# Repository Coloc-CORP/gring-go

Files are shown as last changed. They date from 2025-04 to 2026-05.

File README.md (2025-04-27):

# 💍 Smart BLE Ring Project

---

## 🧠 Team

- 🛠️ **Hardware Engineers**: Mathys Pellen, Pierrick Simon
- 👨‍💻 **Software Engineers**: David Cartier, Marius Chritin

---

## 📜 Project Description

Development of an **ultra-compact smart ring** integrating:
- **Bluetooth Low Energy (BLE) communication**
- **Heart rate (BPM) measurement**
- **Activity and movement tracking**
- **Sleep monitoring**
- **Skin temperature measurement**

Mobile application dedicated to:
- Real-time collection of biometric data
- Visualization and analysis of health information
- Synchronization with **Samsung Health** using **Health Connect API**

---

## 🛠️ Project Architecture

### Hardware
- **Microcontroller**: nRF5340 (Nordic Semiconductor)
- **Main Sensors**:
  - MAX86150: Heart Rate and SpO2
  - BHI260AP: 6-axis IMU (motion detection)
  - MAX30205 (or equivalent): Skin temperature sensor
- **Charging**: Wireless charging with Qi standard (STWLC38 IC)
- **PCB**: Flexible PCB (FPC) for compact integration into a ring
- **Casing**: Titanium ring, machined or 3D printed

### Software
- **Embedded firmware**:
  - Developed with **nRF Connect SDK** (Zephyr RTOS)
  - Standard BLE GATT communication
  - OTA DFU (Firmware update over Bluetooth) supported
- **Android Application**:
  - Developed with **Android Studio**
  - BLE Central communication
  - Integration with **Samsung Health** via **Health Connect**

---

## 📂 Project Folder Structure

```plaintext
/README.md           → Main project documentation
/HW/                 → Hardware designs (schematics, PCB layouts, datasheets)
                     → 3D models of the ring (STEP, STL, F3D formats)
/SW/                 → Embedded firmware for nRF5340 (Zephyr)
                     → Android Studio mobile app project
/doc/                → Specifications, technical documents, research notes
```

---

## 🧩 Technologies and Tools

- **nRF Connect SDK** (Zephyr RTOS, Nordic Semiconductor)
- **Segger Embedded Studio** or **VS Code + nRF Connect Extensions**
- **KiCad** for PCB design
- **OnShape / SolidWorks** for 3D modeling
- **Android Studio** for mobile app development
- **GitHub** for project management and version control

---

## 📈 Roadmap

- [x] Requirements and specifications definition
- [x] Component selection
- [ ] BLE basic firmware development
- [ ] BLE mobile application creation
- [ ] First prototype PCB design
- [ ] Hardware prototype fabrication
- [ ] Full system integration and testing
- [ ] Low-power optimization
- [ ] Final miniaturization and industrialization

---

## ⚡ Inspirations

- Samsung Galaxy Ring
- Oura Ring Gen 3

---

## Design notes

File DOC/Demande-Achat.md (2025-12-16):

## Récapitulatif des composants à acheter

Tous les sites pour acheter chaque composant/carte sont intégrés en hyperlien.

| Composant                | Fonction / Rôle                | Lien / Datasheet / Réf.         | Carte d’évaluation / Dev Kit         |
|--------------------------|-------------------------------|----------------------------------|--------------------------------------|
| nRF5340 (MCU BLE)        | Microcontrôleur principal BLE | [nRF5340](https://www.mouser.fr/ProductDetail/Nordic-Semiconductor/nRF5340-CLAA-R?qs=81r%252BiQLm7BTUbHQUWWib8A%3D%3D&mgh=1&vip=1&utm_id=18189949858&utm_source=google&utm_medium=cpc&utm_marketing_tactic=emeacorp&gad_source=1&gad_campaignid=18189985405&gbraid=0AAAAADn_wf1H5A7hXqZ3Z-MRIcJ73N6WJ&gclid=CjwKCAiA0eTJBhBaEiwA-Pa-hXL2kj0GUdJKz5rNqm_YtVFvSpSPjLrBWhTpHPgSChG9DCrJEowFXRoCWOgQAvD_BwE) | [nRF5340 DK](https://www.mouser.fr/ProductDetail/Nordic-Semiconductor/NRF5340-DK?qs=T94vaHKWudSvpk%2Fi5MmNkA%3D%3D&mgh=1&vip=1&utm_id=18189909961&utm_source=google&utm_medium=cpc&utm_marketing_tactic=emeacorp&gad_source=1&gad_campaignid=18189915556&gbraid=0AAAAADn_wf2LX2m29R1FtorFCg3McUpCX&gclid=CjwKCAiA0eTJBhBaEiwA-Pa-hSZylnIRr_CUexKcZe3W3Hm7M1_NMTNbWYKbaWAjeG-TnCY7hQYBrBoCe3cQAvD_BwE) |
| MAX32664 (PPG)           | Module capteur cardiaque      | [MAX32664](https://www.mouser.fr/ProductDetail/Analog-Devices-Maxim-Integrated/MAX32664GWEA%2bT?qs=MLItCLRbWsyDnR1OLLmFTg%3D%3D) | PCB d'éval conçu, à commander |
| BHI260AP (IMU)           | Accéléro/Gyro 6 axes + MCU    | [BHI260AP](https://www.mouser.fr/ProductDetail/Bosch-Sensortec/BHI260AP?qs=T94vaHKWudTEPTnGI%252BTy9w%3D%3D&srsltid=AfmBOoqDyQJeb3na6sPnhlUFruoI9czkXYRRi1PuOY-V-L53PYxs8R0h) | [BHI260AP Shuttle Board](https://www.mouser.fr/ProductDetail/Bosch-Sensortec/BHI260AP-Shuttle-Board-3.0?qs=sGAEpiMZZMu3sxpa5v1qrpuLb1YRQvRHZemfRhcKQHY%3D) |
| STTS22H (Température)    | Capteur de température        | [STTS22H](https://www.mouser.fr/ProductDetail/STMicroelectronics/STTS22HTR?qs=%252B6g0mu59x7LCfjXXPvLkpg%3D%3D) | [SEN-21262](https://www.mouser.fr/ProductDetail/SparkFun/SEN-21262?qs=9vOqFld9vZWzbY2TLzVlDA%3D%3D&srsltid=AfmBOoovlJG6ulonjrwpkD4eBeJpHDID0WHxTjRv7_asHaaaJilWiW1_) |
| Batterie (test)                | Alimentation                  | [lipo 3.7V 190mAh] https://fr.farnell.com/mikroelektronika/mikroe-2759/batterie-li-ion-3-7v-190mah/dp/2858073   | -                                    |
| DRV2605L (Pilote haptique) | Pilote moteur haptique LRA    | [DRV2605L](https://www.mouser.fr/ProductDetail/Texas-Instruments/DRV2605LTDGSRQ1?qs=bY1dm4K8r4X1ywSIFHWcUw%3D%3D) | [DRV2605L Dev kit](https://fr.rs-online.com/web/p/modules-de-developpement-pour-la-robotique-la-gestion-d-alimentation-et-les-moteurs/1245480?cm_mmc=FR-PLA-DS3A-_-google-_-CSS_FR_FR_PMAX_Catch+All-_--_-1245480&matchtype=&&gclsrc=aw.ds&gad_source=1&gad_campaignid=20578377983&gbraid=0AAAAADkeWNOf1JCgaQc0pjTwe8yyNPBMd&gclid=Cj0KCQiA9OnJBhD-ARIsAPV51xNiMtSwV1MNyEf_7Fm-Ahb4cxmXP-D3dtjudJGbkZPWrh_JE1DPnkkaAiklEALw_wcB) |
| LRA (Moteur haptique)      | Retour haptique (vibration)   | [HD-LA0503-LW28](https://www.mouser.fr/ProductDetail/PUI-Audio/HD-LA0503-LW28?qs=%252BHhoWzUJg4JRddGDY3P1CA%3D%3D) | - |
| Emetteur QI              | Gestion charge sans fil       | [BQ500212A] https://www.mouser.fr/ProductDetail/Texas-Instruments/BQ500212ARGZR?qs=qMm2Sc3MXu62Fost5xc9Dg%3D%3D | PCB d'éval conçu, à commander |
| Recepteur QI             | Gestion charge sans fil       | [BQ51003] https://www.mouser.fr/ProductDetail/Texas-Instruments/BQ51003YFPR?qs=QCUnHQQYO1rRiXeciFj5cA%3D%3D | PCB d'éval conçu, à commander |
| Régulateur / LDO / Chargeur| Régulation tension / charge batterie | [BQ25120A] https://www.mouser.fr/ProductDetail/Texas-Instruments/BQ25120AYFPR?qs=BZBei1rCqCBtbT0X52DCMQ%3D%3D | PCB d'éval conçu, à commander |
| Antenne BLE              | Communication sans fil        | (À définir)                      | Intégré à la carte d'éval nRF5340 DK                                    |

Chaque composant est relié à la carte principale (MCU nRF5340) via des interfaces standards (I²C/SPI pour les capteurs, GPIO pour l’antenne, etc.). Les cartes d’évaluation associées permettent de tester individuellement chaque composant avant intégration sur le PCB final.

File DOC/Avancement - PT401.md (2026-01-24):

*Aperçu de l'avancement au 24 janvier 2026 de notre projet **GRING-GO**.*
## Organisation / documentation

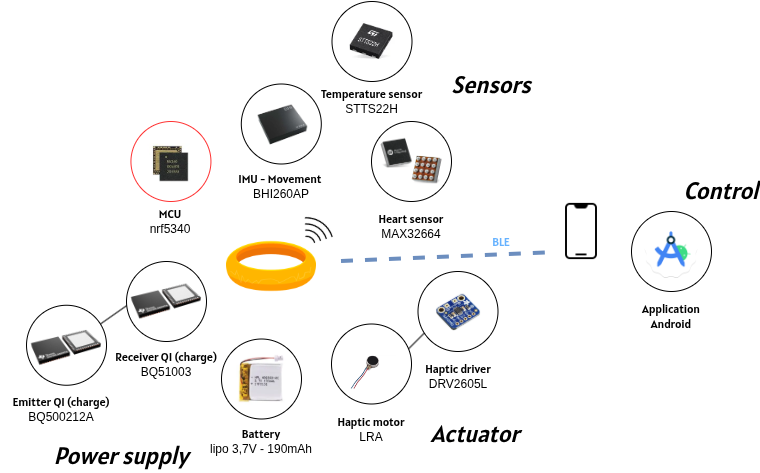
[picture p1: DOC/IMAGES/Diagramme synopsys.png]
Diagramme synopsys.png


Différents documents rédigés : 
- Cahier des charges
- Diagramme de Gantt (organisation + attribution des tâches)
*Vous pouvez retrouver 2 fichiers pdf : Gantt_Gring-go.pdf & Gantt_Gring-go-V2.pdf. La deuxième version incluant les retards.* 
- Répartition horaire

Suivi organisé : [Projet gring-go Github](https://github.com/Coloc-CORP/gring-go)
On retrouve sur ce git le développement entier séparé en différentes branches. L'utilisation des *Tasks*, pour répartir les tâches et avoir une vue d'ensemble de l'état d'avancement du projet.
## Electronique

### Conception des Cartes d'Évaluation Custom

Face à l'indisponibilité ou au coût prohibitif des kits d'évaluation constructeurs officiels, nous avons pris l'initiative de concevoir et produire nos propres solutions de test pour valider les briques technologiques critiques.

#### Conception et Prototypage
Deux cartes d'évaluation spécifiques ont été routées et fabriquées :
* **Module Power & Charge :** Dédié au **BQ25120A** pour valider la régulation du rail 3.0V (indispensable pour le nRF5340) et la gestion de la charge batterie.
* **Module Biométrique :** Support spécifique pour le **MAX32664** et son capteur optique associé, permettant de tester la qualité du signal brut avant l'intégration finale.

#### État de l'Avancement Hardware
* **Statut actuel :** Les circuits imprimés (PCB) et l'ensemble des composants ont été reçus.
* **Phase de Montage :** Nous entamons actuellement le soudage des composants CMS (Composants Montés en Surface).
* **Validation :** Une fois le soudage terminé, nous procéderons aux tests de mise sous tension et à la validation de la communication I2C avec le nRF5340 pour tester "en réel" les drivers précédemment développés.

### Étude de Consommation Théorique

En parallèle du développement, une étude de consommation a été réalisée pour valider la viabilité énergétique du produit.

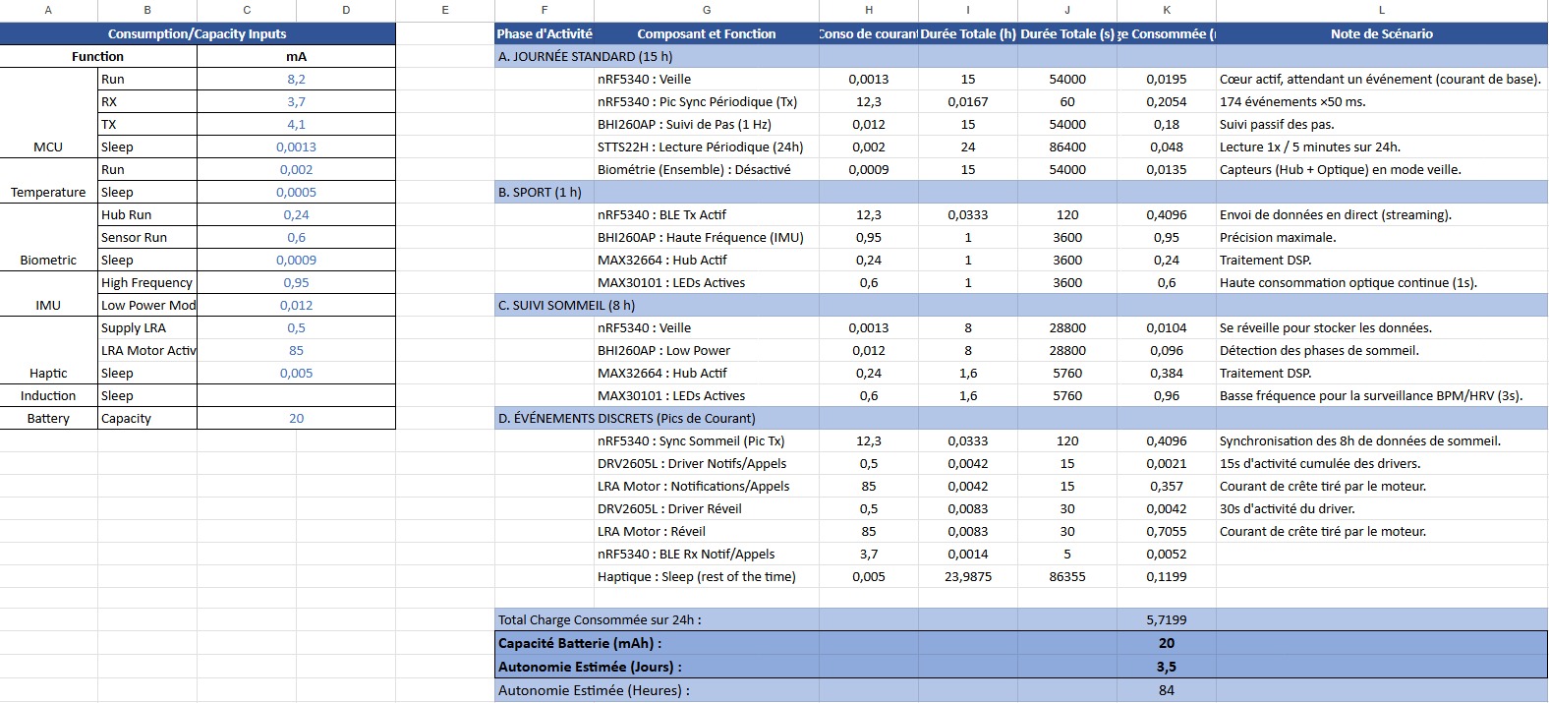
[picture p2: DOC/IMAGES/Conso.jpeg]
Conso


* **Objectif :** Valider une autonomie approximative satisfaisante plutôt que de déterminer une valeur précise dès maintenant.
* **Résultats :** L'étude confirme une autonomie théorique d'environ **3 jours et demi** avec une utilisation normale (polling régulier des capteurs et notifications BLE avec vibration).
* **Validation :** Ce résultat valide les choix d'architecture (rail 3.0V optimisé et modes basse consommation des hubs de capteurs) et assure que le dispositif répond aux attentes qu'on a d'un "wearable".

### Système d'alimentation par induction

Nous avons réalisés une étude comparative sur les modes de transfert d'énergie sans fil, ce qui m'a conduit à valider une architecture basée sur la norme Qi.

#### Architecture système et choix des composants

L'objectif est d'intégrer un système complet dans un volume restreint (type bague connectée). Initialement, l'architecture retenue se décomposait ainsi:

- **Émetteur (Boîtier) :** Utilisation du **BQ500212A**, nécessitant un convertisseur Boost pour stabiliser l'alimentation 5V.
    
- **Récepteur (Bague) :** Le couple **BQ51003** et **BQ25120A** avait été choisi. Le BQ51003 gère la réception , tandis que le BQ25120A fait office de PMIC pour gérer le "Power Path".

Cependant, la conception d'un premier PCB pour ces composants spécifiques a révélé des contraintes de fabrication imprévues : la largeur nécessaire entre les vias était trop faible, rendant le coût de production du PCB prohibitif pour une phase de prototypage.

#### Adaptation pour la phase de test

Afin de valider le fonctionnement sans exploser le budget, j'ai modifié l'architecture pour cette version de test. Sur la partie bague, j'ai remplacé les composants initiaux par un récepteur **BQ51013** couplé à un chargeur **MCP73831T**.

Les cartes d'évaluation constructeur étant trop chères, j'ai conçu mon propre PCB de test sur **KiCad**. Le design est validé et permet de contourner les coûts élevés du premier prototype.

#### Conception hardware et dimensionnement

Le travail de conception s’est concentré sur l'optimisation de l'antenne et de la résonance :

- **Bobinage :** J'utilise du fil de cuivre de 0,22 mm. L'idée est de réaliser un montage type "fil de Litz" pour limiter l'effet de peau et maximiser le passage du courant à haute fréquence.
    
- **Accord de fréquence :** L’étape critique est le calcul des condensateurs de résonance $C_1$ et $C_2$ pour accorder l'antenne sur la fréquence cible de 100 kHz. L’ajout de feuilles de ferrite est également prévu pour canaliser le flux.

#### Prochains pas

Le PCB de test sur KiCad est réussi. Actuellement, je suis en attente de la réception des composants pour lancer l'assemblage. Pour effectuer les premiers essais de charge, j'ai également commandé une petite batterie LiPo, en sélectionnant le modèle le moins cher et le plus compact possible.

## Software

### Programmation embarqué

#### Développement embarqué NRF5340

Le développement logiciel repose sur le processeur **nRF5340** (Dual-core ARM Cortex-M33). L'architecture a été conçue pour être modulaire sous **Zephyr RTOS**, en respectant notre diagramme UML qui sépare strictement la gestion des périphériques de la logique applicative.

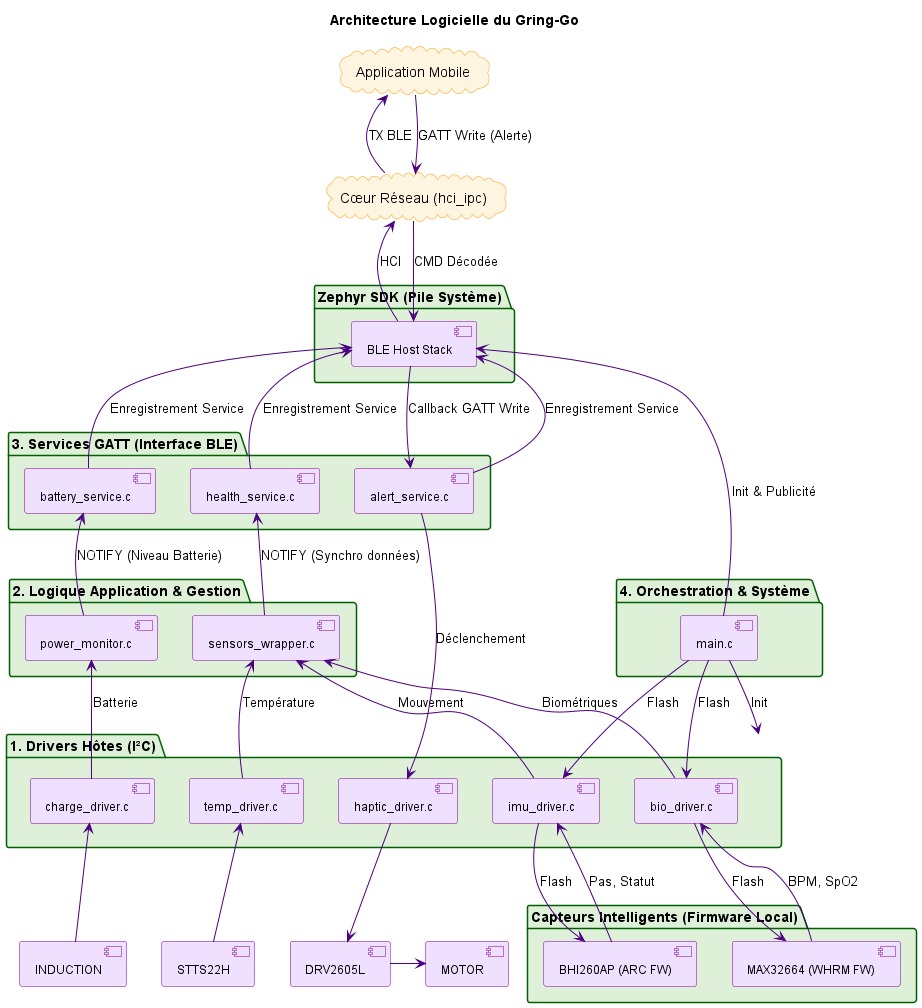
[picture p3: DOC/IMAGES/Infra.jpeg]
Infra


*Ce diagramme UML a été réalisé par l'écriture d'un code PlantUML.*

##### Travaux Réalisés : Couche Drivers
La phase de développement des drivers de bas niveau est désormais terminée. Ce travail a inclus :
* **Communication I2C & Comportement :** Écriture des drivers pour l'IMU (**BHI260AP**), le capteur biométrique (**MAX32664**), le capteur de température (**STTS22H**) et le gestionnaire de charge (**BQ25120A**).
* **Injection de Code (Sensor Fusion) :** Implémentation de la logique d'injection des données accélérométriques de l'IMU vers le capteur cardiaque pour la compensation de mouvement, garantissant la précision des mesures lors d'activités physiques.
* **Gestion de l'Énergie :** Configuration des registres pour optimiser l'autonomie (Deep Sleep, Ship Mode).
* ...

##### Prochaines Étapes : Intégration et Bluetooth
Le code est prêt pour la phase de tests réels sur les composants. La suite du développement portera sur :
* **Communication BLE :** Développement de la stack Bluetooth Low Energy.
* **Synchronisation Application :** Travail en collaboration avec **David** pour mapper les structures de données sur les services GATT afin d'assurer une communication fluide avec l'application mobile en cours de développement.

### Application Android

L'application Android est développé en JAVA sur Android Studio. 
Nous sommes passés sur une première phase de réflexion de l'architecture avec la définitions des différents *fragments* de l'application, c'est à dire les différentes fenêtres.

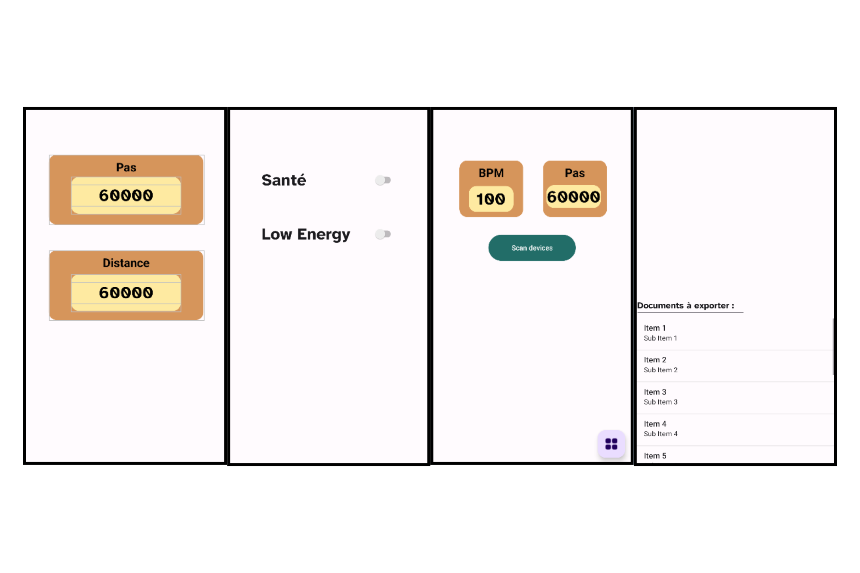
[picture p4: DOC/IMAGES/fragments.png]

*Différents fragments créés 

Les fonctions de découverte Bluetooth à été mise en place. Le reste de la communication va se baser sur [Android-BLE-Library](https://github.com/NordicSemiconductor/Android-BLE-Library). 

Suite à l'appui du bouton *Scan Devices*, la liste d'appareils bluetooth apparaît et l'on peut choisir l'appareil bluetooth auquel s'appairer (le nrf5340). 

On retrouve une autre thématique qui est l'autorisation de permissions. 

## Retards (justification)

On retrouve de légers retards sur 2 points : 
- La partie hardware avec notamment l'alimentation boitier : celle-ci a pris du retard avec l’absence de composants.
- L'application Android est plus lente à développer que prévu car c'est un nouvel environnement sur lequel nous débutons. C'est pour cela que le temps d'adaptation n'est pas a négligé

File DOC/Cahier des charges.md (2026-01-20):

## Introduction

La formation d'ingénieur de l'ESISAR est une formation permettant de de construire les connaissances et compétences de l'ingénieur que celui-ci pourra être confronté dans sa carrière professionnelle. Cela est fait de différentes façon lors des différents cours suivis dans l'école mais la formation passe par une étape très importante : la mise en situation réelle.

Etre en entreprise, c'est faire continuellement des *projets*. En effet, ce sont autour de ces entités que grand nombre d'entre nous naviguent en entreprise. Ceux-ci se déroulent en plusieurs étapes et requièrent un large spectre de compétences pour les mettre à bien.

Le projet, choisi par nous-mêmes, est le projet d'une bague connectée que l'on appelle *Gring-Go*. Le travail va être effectué en passant de la spécification du projet au développement des différentes composantes, en passant par les différents tests démonstratifs pour enfin avoir un produit complet répondant aux différentes problématiques.

C'est un projet qui se déroule sur 9 semaines avec un nombre d'heures alloué au projet d'une centaine d'heures pour chaque collaborateur.

---
## Objectifs

### Objectifs principaux
-  Avoir un suivi des données corporelles en temps réel
-  Pouvoir interagir avec la bague via un système Android
-  Choisir les composants adéquats pour la réalisation du cahier des charges
-  Avoir un suivi des données corporelles dans le temps
-  Notifier sensoriellement l'utilisateur lors d'évenements sur le téléphone 
-  Avoir un gabarit adapté à l'utilisation en tant que bague

### Objectifs transverses
-  Conduire l'organisation et le management du projet de bout en bout
-  Renforcer ses compétences techniques en autonomie

---
## Diagramme du projet

Diagramme synopsys.png

---
## Description fonctionnelle

1. FP : Le produit doit permettre à l'utilisateur de suivre ces données biométriques.

2. FP : Le produit doit permettre à l'utilisateur de suivre ces données d'activité physique.
3. FP : Le produit doit permettre à l'utilisateur d'être notifier d'évênements sur le téléphone.
4. FC : Le produit doit être confortable à porter (forme agréable, matériau confortable)
5. FC : L'autonomie du produit doit être suffisamment élevé (1 semaine d'autonomie).
6. FC : La distance de communication doit être suffisamment élevé (5 m)
7. FC : Le produit doit être convenablement réactif (mesures <1 min)

*Provisoire*
1. FP : Le produit doit permettre à l'utilisateur de suivre son sommeil
2. FP : Le produit doit permettre à l'utilisateur d'avoir un indicateur sur son stress

3. FC : Le produit doit être résistant à l'eau (IP)
4. FC : Le produit peut se charger sans fil (charge par induction)

---
## Budget

Un budget entre 300 et 400 € à été annoncé pour la réalisation du projets (matériel, prestations, composants).

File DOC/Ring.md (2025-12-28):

# 💍 Projet Bague Connectée BLE - Santé & Bien-être

## 🎯 Objectif

Créer une **bague connectée** ultra-compacte, élégante et rechargeable sans fil, capable de :
- Suivre la fréquence cardiaque
- Mesurer la SpO2 (oxygène dans le sang)
- Évaluer le stress
- Compter les pas et suivre l’activité physique
- Suivre les phases de sommeil
- Mesurer la température corporelle
- Se connecter à Samsung Health via Bluetooth Low Energy (BLE)

---

## 🧩 Architecture générale

| Composant                  | Fonction                                                     |
| -------------------------- | ------------------------------------------------------------ |
| **nRF5340 (Nordic)**       | Microcontrôleur principal avec BLE                           |
| **MAX86150 / MAX30102**    | Capteur PPG (fréquence cardiaque, SpO2, stress)              |
| **BHI260AP / LSM6DSOX**    | IMU pour mouvement, podomètre, détection du sommeil          |
| **STTS22H**                | Capteur de température corporelle                            |
| **Batterie LiPo 10-20mAh** | Alimentation, rechargeable sans fil                          |
| **STWLC38**                | Récepteur de recharge sans fil (Qi) avec protection intégrée |
| **PCB flexible (FPC)**     | Support du circuit miniature                                 |
| **Boîtier titane**         | Enveloppe solide, légère et hypoallergénique                 |

---

## 🔋 Alimentation & Recharge

- **Recharge sans fil Qi** via un chargeur personnalisé
- Basé sur **STWLC38**, compatible Qi 1.2, avec protection intégrée
- Antenne bobinée sur FPC autour de la bague
- Batterie : **LiPo 3.7V** entre 10 et 20 mAh, charge lente pour préserver la durée de vie

---

## 📱 Fonctionnalités principales

| Fonction                      | Capteurs nécessaires                     | Détail technique                                   |
|-------------------------------|------------------------------------------|---------------------------------------------------|
| Fréquence cardiaque           | MAX86150 / MAX30102                      | PPG infrarouge, données envoyées en BLE           |
| SpO2                          | MAX86150 / MAX30102                      | Analyse des variations d’intensité lumineuse      |
| Stress / HRV                  | PPG                                      | Analyse de la variabilité cardiaque (HRV)         |
| Suivi des pas (podomètre)     | BHI260AP / LSM6DSOX                      | Accéléromètre et algorithmes de step counting     |
| Suivi de sommeil (phases)     | PPG + IMU                                | Fusion des données pour estimer les cycles        |
| Température corporelle        | STTS22H                                  | Mesure en contact avec la peau (intérieur bague)  |

---

## 📶 Connexion à Samsung Health

- **BLE Standard HRM (Heart Rate Monitor Profile)** reconnu par Samsung Health
- Via **nRF Connect SDK** (Zephyr RTOS) ou Nordic SDK
- Possibilité de développer une **application Android compagnon** pour collecter, afficher et éventuellement **transférer via Health Connect** les données vers Samsung Health

---

## 🛠️ Logiciels & Développement

- **Firmware :**
  - **nRF Connect SDK** avec Zephyr RTOS (Langage C)
  - IDE recommandé : **nRF Connect for VS Code** ou **Segger Embedded Studio**
- **Conception PCB :**
  - Outils : **KiCad**, **Altium Designer**
  - Type : **Flexible PCB (FPC)** ultra-fin
- **Modélisation 3D du boîtier :**
  - Fusion 360 / SolidWorks
  - Impression SLA ou CNC pour prototypage
  - Matériau : **Titane** (durable, hypoallergénique)

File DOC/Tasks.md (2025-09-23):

# Découpage des tâches et estimations de temps - Projet Gring-Go
## Mathys : 

- Orga : 7H
  - Identification des grandes parties et objectifs du projet : 2H
  - Répartition de la charge de travail : 1H
  - Découpage des taches : 1.5H
  - Estimation de temps des tâches et Gantt : 2.5H
- DOC : 13H
  - Cahier des charges : 3H
  - Spécifications : 2H
  - Hardware Design Description : 10H
- HW : 12H
  - Choix des composants : 12H
    - Accélero / Podo : 2H
    - PPG / Sp02 : 2H
    - Temperature : 2H
    - Microcontroleur : 2H
    - HP ou Micro ? : 2H
    - Antenne BLE : 2H
- SW : 32H
  - Embarqué : 32H
    - Traitement des données capteurs : 9H
      - PPG : 3H
      - Accéléro : 3H
      - Temp : 3H
    - Communication capteur / micro : 4H
    - Commande de l'actionneur (HP ou micro) : 7H
    - Communication des données vers Appli : 5H
      - Transmission des données capteurs : 2.5H
      - Réception de commandes : 2.5H
    - Gestion énergétique : 7H
      - Implémentation des modes de veille du micro : 3H
      - Gestion des capteurs : 4H
- Modélisation 3D : 33H
  - Plans de la bague : 5H
  - Modèle : 28H
- Etude de consommation : 13H
  - Etablir un plan de mesures de consommations : 2H
  - Réaliser les mesures : 7H
  - Interpréter les mesures et les documenter : 4H 

TOTAL : 110H

TOTAL D'HEURES EN SEANCES : 28H + 28H = 56H

TOTAL D'HEURES EN PERSO : 54H

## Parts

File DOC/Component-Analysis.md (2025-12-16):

# 📊 Component Comparison Tables — Smart Ring Project

---

## 1. Microcontroller (MCU BLE)

| Model            | Dimensions (mm) | Mass | Consumption (Active / Sleep) | Supply Voltage | Flash / RAM | Interfaces | Special Features | Eval Kit Availability | Price (€) | Notes |
|------------------|-----------------|------|------------------------------|----------------|-------------|------------|------------------|-----------------------|-----------|-------|
| **nRF5340** (Nordic) |                 |      |                              |                |             |            |                  |                       |           | Le plus utilisé sur le marché pour les memes usages donc aussi le plus de commu pour de l'aide potentielle dans forums, possède toutes les fonctions nécessaires + multi thread + RTOS |
|                  |                 |      |                              |                |             |            |                  |                       |           |       |
|                  |                 |      |                              |                |             |            |                  |                       |           |       |

---

## 2. Heart Rate Sensor (PPG + Sp0²)

| Model                     | Dimensions (mm)    | Mass | Consumption (Act / Sleep) | Supply Voltage    | Interface | Acc / Perf | Integrated LEDs | Module / Sensor | VIL / VIH        | Price (€) | Notes |
|---------------------------|--------------------|------|---------------------------|-------------------|-----------|------------|-----------------|-----------------|------------------|-----------|-------|
| **MAX32664** (Analog Devices) | 3.87 x 3.87 x 0.64 | 22mg |                           | 1.71 - 3.63V      | I²C / SPI |            | No              | Module          | 0.3 / 0.7 VDD    | 6.12      | Besoin d'un capteur optique avec données brutes en sortie |
| MAX30101 (Analog Devices) | 5.6  x 3.3  x 1.55 | 33mg | **0.6mA / 0.7µA**             | 1.7 - 2V (5V LED) | I²C       | 18-bits    | Yes             | Sensor          | 0.3 / 0.7 VDD    | 10.23     | **PIM438**| 
| NJL5313R (Nisshinbo)      | 3.15 x 6.00 x 0.65 | **17mg** | 15mA                      | 3.5V              | -         |            | Yes             | Sensor          | -                | 5.18      | Consomme trop et mauvaise disponibilité      |

---

## 3. IMU (Accelerometer + Gyroscope)

| Model            | Dimensions (mm)    | Mass | Consumption (Active / Sleep) | Supply Voltage | Interface | Axes | Accuracy | VIL / VIH        | Price (€) | Notes |
|------------------|--------------------|------|------------------------------|----------------|-----------|------|----------|------------------|-----------|-------|
| **BHI260AP (Bosch)** | 3.6 x 4.1 x 0.83   |      | 249µA / 8µA                  | 1.8V           | I²C / SPI | 6    |          | 0.3 / 0.7 VDD    | 6.05      | **MCU intégré qui traite localement les données : beaucoup plus simple à implémenter**, Dev board 13$ |
| LSM6DSOX (ST)    |**2.5 x 3   x 0.83**|      | **170-26µA  / 3µA**          | 1.7 - 3.6V     | I²C / SPI | 6    |          | 0.3 / 0.7 VDD    | **3.62**  | ABX00101 10$, STEVAL 15$      |
|                  |                    |      |                              |                |           |      |          |                  |           |       |

---

## 4. Temperature Sensor

| Model        | Dimensions (mm) | Mass | Consumption  | Supply Voltage | Interface   | Accuracy | Special Features | Price (€) | Notes |
|--------------|-----------------|------|--------------|----------------|-------------|----------|------------------|-----------|-------|
| **STTS22H (ST)** | 2.0 x 2.0 x 0.5 |      | **120 / 1.75 µA**| 1.5 - 3.6      | I²C / SMBus | 0.25°C   |                  | 1.45      | **SEN-21262 6$**|
| TMP117       | **1.5 x 0.95 x 0.5**|      | 135 / 3.5 µA | 1.7 - 5.5      | I²C / SMBus | **0.1°C**    |                  | 1.92      | SEN-15805 17$, ADA4821 14$      |

---

## 5. Battery

| Model | Capacity (mAh) | Mass | Dimensions (mm) | Thickness (mm) | Voltage (Nominal / Range) | Protection Circuit | Certification | Price (€) | Notes |
|-------|----------------|------|-----------------|----------------|---------------------------|--------------------|---------------|-----------|-------|
|       |                |      |                 |                |                           |                    |               |           |       |
|       |                |      |                 |                |                           |                    |               |           |       |

---

## 6. Wireless Charging IC

| Model | Dimensions (mm) | Mass | Supply Voltage | Output Voltage | Efficiency | Qi Standard Support | Features | Price (€) | Notes |
|-------|-----------------|------|----------------|----------------|------------|---------------------|----------|-----------|-------|
|       |                 |      |                |                |            |                     |          |           |       |
|       |                 |      |                |                |            |                     |          |           |       |

---

## 7. Wireless Charging Coil

| Model | Diameter (mm) | Mass | Thickness (mm) | Inductance (µH) | Resistance (Ω) | Efficiency | Compatible ICs | Price (€) | Notes |
|-------|---------------|------|----------------|-----------------|----------------|------------|----------------|-----------|-------|
|       |               |      |                |                 |                |            |                |           |       |
|       |               |      |                |                 |                |            |                |           |       |

---

## 8. Regulator / LDO

| Model | Dimensions (mm) | Output Voltage | Quiescent Current | Dropout Voltage | Max Current | Noise Level | Price (€) | Notes |
|-------|-----------------|----------------|-------------------|-----------------|-------------|-------------|-----------|-------|
|       |                 |                |                   |                 |             |             |           |       |
|       |                 |                |                   |                 |             |             |           |       |

---

## 9. BLE Antenna

| Model | Type (Ceramic / PCB) | Dimensions (mm) | Mass | Gain (dBi) | Frequency | Matching Required | Price (€) | Notes |
|-------|----------------------|-----------------|------|------------|-----------|-------------------|-----------|-------|
|       |                      |                 |      |            |           |                   |           |       |
|       |                      |                 |      |            |           |                   |           |       |

## 10. Actionneur (Comparaison)

| Actionneur | Mode de Fonctionnement | Avantages pour une Bague | Inconvénients / Impact Physique | Choix |
| :--- | :--- | :--- | :--- | :--- |
| **Moteur Haptique (LRA/ERM)** | Vibration discrète | **Retour personnel et silencieux.** Faible consommation cumulée (pics courts). | Nécessite un volume minimal (épaisseur) et un driver (DRV2605L). | **CHOISI** |
| **Haut-Parleur / Buzzer** | Son / Alerte audible | Peut attirer l'attention de l'utilisateur sans contact. | **Nécessite une chambre acoustique.** Retour non-discret (entendue par l'entourage). Haute consommation continue. | REJETÉ |
| **Microphone** | Acquisition audio | Permet la commande vocale ou l'enregistrement (si requis). | **Non un actionneur.** Nécessite un ADC / DSP pour le traitement et une forte consommation. | REJETÉ |

---

## 11. Composants Haptiques 

| Model | Dimensions (mm) | Mass | Consumption (Active / Sleep) | Supply Voltage | Interface | Special Features | Eval Kit Availability | Price (€) | Notes |
|---|---|---|---|---|---|---|---|---|---|
| **Pilote DRV2605L (TI)** | 1.5 x 1.5 x 0.6 | | **0.5 mA / 4.1 µA** | 1.8 - 3.3V | I²C | Bibliothèque de 123 effets ROM intégrée. | DRV2605LEVM (Abordable) | 2.15 | Utilisation du mode Bibliothèque pour décharger le nRF5340. |
| **Moteur LRA** (Ex: HD-EMC0503-LW27) | $5 \text{ x } 1.8$ (épaisseur) | < 1g | **85 mA** (pic) | 2.7 - 3.3V | PWM | Le seul LRA compatible avec l'épaisseur d'une bague. | N/A | 1.50 | Courant de pointe important (85 mA) mais très courte durée (Duty Cycle faible). |

---

## Final choices

| **Component** | **Dimensions (mm)** | **Consumption (Active / Sleep)** | **Supply Voltage** | **Interface** | **Accuracy / Performance** | **Special Features** | **Price (€)** | **Notes** |
|---------------|----------------------|----------------------------------|---------------------|---------------|-----------------------------|-----------------------|---------------|-----------|
| MCU           | nRF5340              |                                  |                     |               |                             | Multi-thread, RTOS    |               | Le plus utilisé sur le marché, grande communauté |
| Heart Sensor (PPG) | MAX32664          |                                  | 1.71 - 3.63V        | I²C / SPI     |                            | Besoin d'un capteur optique, données brutes | 6.12          | Module, nécessite capteur optique externe |
| IMU           | BHI260AP             | 249µA / 8µA                    | 1.8V         | I²C / SPI     | 6 axes                     |                      | 6.05          | **MCU intégré qui traite localement les données : beaucoup plus simple à implémenter**, Dev board 13$ |
| Temp Sensor   | STTS22H              | 120 / 1.75 µA                     | 1.5 - 3.6V         | I²C / SMBus   | 0.25°C                      |                      | 1.45          | SEN-21262 6€ |
| **Haptic Driver** | **DRV2605L** | **0.5 mA / 4.1 µA** | **1.8 - 3.3V** | **I²C** | **N/A** | **Bibliothèque ROM intégrée** | **2.15** | Pilote basse consommation pour décharger le MCU. |
| **Haptic Motor** | **LRA** | **85 mA / 0 mA** | **2.7 - 3.3V** | **PWM** | **Discret** | **Ultra-plat (1.8mm)** | **1.50** | Courant de pointe important mais durée d'activation très courte. | Battery       |                      |                                  |                     |               |                             |                       |               |           |
| Wireless Charging IC |                |                                  |                     |               |                             |                       |               |           |
| Charging Coil |                      |                                  |                     |               |                             |                       |               |           |
| Regulator / LDO |                     |                                  |                     |               |                             |                       |               |           |
| BLE Antenna   |                      |                                  |                     |               |                             |                       |               |           |
| Other         |                      |                                  |                     |               |                             |                       |               |           |

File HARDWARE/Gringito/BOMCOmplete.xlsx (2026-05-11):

Quantité | Références | Type | Valeur / MPN | Boîtier | Spécifications et Filtres (Mouser / Digi-Key) | ref | Ref mouser | Prix | Stock ? | A commander | Prix a commander
1 | U4 | Puce | BQ500212ARGZR | VQFN-48 | Contrôleur Émetteur Qi |  | https://www.mouser.fr/c/?q=BQ500212ARGZR | 7.62 | 6 | 0 | 0
1 | U6 | Puce | BQ51013BRHLR | VQFN-20 | Contrôleur Récepteur Qi |  | https://www.mouser.fr/ProductDetail/Texas-Instruments/BQ51013BRHLR | 3.1 | 1 | 2 | 6.2
2 | U3, U5 | Puce | CSD97376Q4M | VSON-8 | Power Stage NexFET |  | https://www.mouser.fr/ProductDetail/Texas-Instruments/CSD97376Q4M?qs=7GxONfNUZSgNG7s2u94qUg%3D%3D | 1.85 | 0 | 6 | 11.1
2 | U1, U8 | Puce | PTPS7A2033PDBVR | SOT-23-5 | LDO 3.3V |  | https://www.mouser.fr/ProductDetail/Texas-Instruments/TPS7A2033PDBVR?qs=hd1VzrDQEGjk%2FOBnRfKB4A%3D%3D | 0.275 | 0 | 6 | 1.65
1 | U2 | Puce | INA199A1DCKR | SC-70-6 | Amplificateur de mesure de courant |  | https://www.mouser.fr/ProductDetail/Texas-Instruments/INA199A1DCKR?qs=v3hU%2FV0XOahkyIKIBScY5Q%3D%3D | 0.499 | 0 | 3 | 1.497
1 | U7 | Puce | MCP73831T-2ATI/OT | SOT-23-5 | Chargeur Li-Ion |  | https://www.mouser.fr/ProductDetail/Microchip-Technology/MCP73831T-2ATI-OT?qs=yUQqVecv4qsZbioEUu%252B83g%3D%3D | 0.654 | 1 | 2 | 1.308
1 | C7 | Condensateur | 33pF | 805 | Diélectrique C0G/NP0, Tension 50V min | VJ0805A330KXAAC | https://www.mouser.fr/ProductDetail/Vishay-Vitramon/VJ0805A330KXAAC?qs=%252BzNVVDDlEaF%2FJI7KaxLPoQ%3D%3D | 0.189 | 0 | 10 | 1.89 | Prix total
2 | C12, C17 | Condensateur | 4.7nF (4700pF) | 805 | Diélectrique C0G/NP0, Tension 50V min | CGA4C2C0G1H472J | https://www.mouser.fr/ProductDetail/TDK/CGA4C2C0G1H472J060AA?qs=FxQuwy19cyCgdYzJw5%252BHfA%3D%3D | 0.071 | 0 | 20 | 1.42 | 63.223
4 | C1, C20, C36, C42 | Condensateur | 0.01µF (10nF) | 805 | Diélectrique C0G/NP0, Tension 50V min | CGA4C2C0G1H103J | https://www.mouser.fr/ProductDetail/TDK/C2012C0G1H103J060AA?qs=dfay7wIA1uESihXTlxZAiQ%3D%3D | 0.103 | 0 | 20 | 2.06
2 | C32, C44 | Condensateur | 22nF | 805 | Diélectrique C0G/NP0, Tension 50V min | CGA4J2C0G1H223J | https://www.mouser.fr/ProductDetail/TDK/CGA4J2C0G1H223J125AA?qs=NRhsANhppD%252B%2Fmt276RAXag%3D%3D | 0.12 | 0 | 10 | 1.2
2 | C34, C43 | Condensateur | 0.47µF (470nF) | 805 | Diélectrique X7R, Tension 50V min | C0805C474J5REC7210 | https://www.mouser.fr/ProductDetail/KEMET/C0805C474J5REC7210?qs=55YtniHzbhBIB%252B2OjgsYHA%3D%3D | 0.153 | 0 | 10 | 1.53
5 | C37, C38, C39, C40, C41 | Condensateur | TDB | 805 | Prévoir des assortiments C0G de quelques nF pour le réglage au labo |  |  |  |  |  | 0
5 | Pour C37 à C41 | Condensateur | 2.2 nF (2200 pF) | 805 | Diélectrique C0G/NP0, Tension 50V min | CGA4J3C0G2E222J | https://www.mouser.fr/ProductDetail/TDK/CGA4J3C0G2E222J125AA?qs=FxQuwy19cyAnpWAkJxMUqQ%3D%3D | 0.093 |  | 10 | 0.93
5 | Pour C37 à C41 | Condensateur | 1 nF (1000 pF) | 805 | Diélectrique C0G/NP0, Tension 50V min | AC805JRNPO0BN102 | https://www.mouser.fr/ProductDetail/YAGEO/AC0805JRNPO0BN102?qs=WS5Jv%252B%252Bx1qWv6SGJfntmZw%3D%3D | 0.089 | 0 | 10 | 0.89
5 | Pour C37 à C41 | Condensateur | 470 pF | 805 | Diélectrique C0G/NP0, Tension 50V min | CC0805JPNPO9BN471 | https://www.mouser.fr/ProductDetail/YAGEO/CC0805JPNPO9BN471?qs=7s%252B3O6pAiyArhfcZRyQSXQ%3D%3D | 0.037 | 0 | 10 | 0.37
5 | Pour C37 à C41 | Condensateur | 220 pF | 805 | Diélectrique C0G/NP0, Tension 50V min | CGA4C4C0G2W221J060AA | https://www.mouser.fr/ProductDetail/TDK/CGA4C4C0G2W221J060AA?qs=Zt%252BKPUOg4ocV%252BjuYZYAGHQ%3D%3D | 0.077 | 0 | 10 | 0.77
5 | Pour C37 à C41 | Condensateur | 100 pF | 805 | Diélectrique C0G/NP0, Tension 50V min |  | AVEC C16 C18 |  |  |  | 0
5 | Pour C37 à C41 | Condensateur | 47 pF | 805 | Diélectrique C0G/NP0, Tension 50V min | C0805C470JDGACTU | https://www.mouser.fr/ProductDetail/KEMET/C0805C470JDGACTU?qs=HkDAmeg8w%252BfhZX5bPX%2F3Fg%3D%3D | 0.19 | 0 | 10 | 1.9
5 | Pour C37 à C41 | Condensateur | 22 pF | 805 | Diélectrique C0G/NP0, Tension 50V min | VJ0805A220JXCCW1BC | https://www.mouser.fr/ProductDetail/Vishay-Vitramon/VJ0805A220JXCCW1BC?qs=5N7VPDfziMRebYDFq5t7Jw%3D%3D | 0.12 | 0 | 10 | 1.2
4 | C2, C13, C25, C29 | Condensateur | 10µF | 805 | Diélectrique X5R ou X7R, Tension 50V min | GRM21BR61H106KE43L | https://www.mouser.fr/ProductDetail/Murata-Electronics/GRM21BR61H106KE43L?qs=lYGu3FyN48cBZlIduWKclg%3D%3D | 0.109 | 0 | 20 | 2.18
2 | C9, C14 | Condensateur | 4.7µF | 805 | Diélectrique X5R ou X7R, Tension 25V min | CGA4J1X7R1H475K125AC | https://www.mouser.fr/ProductDetail/TDK/CGA4J1X7R1H475K125AC?qs=PqoDHHvF64%252BmskN2S82T2g%3D%3D | 0.224 | 0 | 10 | 2.24
12 | C3, C4, C8, C10, C15, C22, C26, C27, C30, C31, C33, C35 | Condensateur | 1µF | 805 | Diélectrique X7R, Tension 25V min | C2012X7R1H105K | https://www.mouser.fr/ProductDetail/TDK/C2012X7R1H105K125AB?qs=NRhsANhppD9AlYlb8kBg7Q%3D%3D | 0.099 | 0 | 30 | 2.97
6 | C5, C6, C11, C23, C24, C28 | Condensateur | 0.1µF (100nF) | 805 | Diélectrique X7R, Tension 50V min | KAF21KR72A104KL | https://www.mouser.fr/ProductDetail/KYOCERA-AVX/KAF21KR72A104KL?qs=Jm2GQyTW%2FbiUCISqVwD%2FLA%3D%3D | 0.101 | 0 | 20 | 2.02
4 | C16, C18, C19, C21 | Condensateur | 0.1µF (100nF) | 1206 | Diélectrique C0G/NP0, Tension 50V min | C3216C0G2A104J6C | https://www.mouser.fr/ProductDetail/TDK/C3216C0G2A104J160AC?qs=sO%2FZ8XQFeM2ox3y9zt3TJw%3D%3D | 0.362 | 0 | 20 | 7.24
1 | R3 | Résistance | 20 mΩ | 805 | Tolérance 1%, Current Sense, Puissance 0.25W ou 0.5W | 652-CFN0805FXR020ELF | https://www.mouser.fr/ProductDetail/Bourns/CFN0805-FX-R020ELF?qs=gZXFycFWdAOZ7fJXWmOzdA%3D%3D | 0.344 | 0 | 3 | 1.032
5 | R13, R15, R18, R19, R20 | Résistance | 56.2 kΩ | 805 | Tolérance 1% 50 PPM 0.125W | RGC1/10C5622FTP | https://www.mouser.fr/ProductDetail/Kamaya/RGC1-10C5622FTP?qs=GedFDFLaBXGddNBPdrL7hA%3D%3D | 0.082 | 0 | 20 | 1.64
1 | R9 | Résistance | 12.1 kΩ | 805 | Tolérance 1% 50 PPM 0.125W | RT0805FRE0712K1L | https://www.mouser.fr/ProductDetail/YAGEO/RT0805FRE0712K1L | 0.014 | 0 | 10 | 0.14
1 | R12 | Résistance | 76.8 kΩ | 805 | Tolérance 1% 50 PPM 0.125W | RT0805FRE0776K8L | https://www.mouser.fr/ProductDetail/YAGEO/RT0805FRE0776K8L | 0.013 | 0 | 10 | 0.13
1 | R26 | Résistance | 140 Ω | 805 | Tolérance 1% 50 PPM 0.125W | RT0805FRE07140RL | https://www.mouser.fr/ProductDetail/YAGEO/RT0805FRE07140RL?qs=sGAEpiMZZMvdGkrng054t98Xz4DA4UW4bFW4LYzjMtg%3D | 0.014 | 0 | 10 | 0.14
1 | R28 | Résistance | 360 Ω | 805 | Tolérance 1% 50 PPM 0.125W | RT0805FRE07360RL | https://www.mouser.fr/ProductDetail/YAGEO/RT0805FRE07360RL?qs=sGAEpiMZZMvdGkrng054t98Xz4DA4UW4S2KRqZkM0LQ%3D | 0.014 | 0 | 10 | 0.14
2 | R2, R4 | Résistance | 1 Ω | 805 | Tolérance 1% 50 PPM 0.125W | RT0805FRE131RL | https://www.mouser.fr/ProductDetail/YAGEO/RT0805FRE131RL | 0.026 | 0 | 10 | 0.26
2 | R5, R10 | Résistance | 10 Ω | 805 | Tolérance 1% 50 PPM 0.125W | RE0805FRE0710RL | https://www.mouser.fr/ProductDetail/YAGEO/RE0805FRE0710RL | 0.015 | 0 | 10 | 0.15
2 | R24, R25 | Résistance | 470 Ω | 805 | Tolérance 1% 50 PPM 0.125W | RT0805FRE13470RL | https://www.mouser.fr/ProductDetail/YAGEO/RT0805FRE13470RL | 0.012 | 0 | 10 | 0.12
1 | R1 | Résistance | 1 kΩ | 805 | Tolérance 1% 50 PPM 0.125W | RT0805FRE101KL | https://www.mouser.fr/ProductDetail/YAGEO/RT0805FRE101KL | 0.014 | 0 | 10 | 0.14
2 | R21, R22 | Résistance | 3.6 kΩ | 805 | Tolérance 1% 50 PPM 0.125W | RT0805FRE073K6L | https://www.mouser.fr/ProductDetail/YAGEO/RT0805FRE073K6L?qs=sGAEpiMZZMvdGkrng054t98Xz4DA4UW4H0sQAQZ78zw%3D | 0.014 | 0 | 10 | 0.14
2 | R6, R7 | Résistance | 5.1 kΩ | 805 | Tolérance 1% 50 PPM 0.125W | RT0805FRE075K1L | https://www.mouser.fr/ProductDetail/YAGEO/RT0805FRE075K1L | 0.013 | 0 | 10 | 0.13
5 | R8, R14, R16, R23, R27 | Résistance | 10 kΩ | 805 | Tolérance 1% 50 PPM 0.125W | RE0805FRE1010KL | https://www.mouser.fr/ProductDetail/YAGEO/RE0805FRE1010KL | 0.022 | 0 | 20 | 0.44
1 | R29 | Résistance | 33 kΩ | 805 | Tolérance 1% 50 PPM 0.125W | RT0805DRE0733KL | https://www.mouser.fr/ProductDetail/YAGEO/RT0805DRE0733KL?qs=sGAEpiMZZMvdGkrng054t98Xz4DA4UW4E2crgyBxdeA%3D | 0.019 | 0 | 10 | 0.19
1 | R11 | Résistance | 100 kΩ | 805 | Tolérance 1% 50 PPM 0.125W | RT0805DRE07100KL | https://www.mouser.fr/ProductDetail/YAGEO/RT0805DRE07100KL?qs=sGAEpiMZZMvdGkrng054t98Xz4DA4UW4obdZ51RqQ4E%3D | 0.019 | 0 | 10 | 0.19
1 | R17 | NTC | 10 kΩ à 25°C | 805 | Thermistance NTC, Beta (B) proche de 3380K | B57442V5103J62 | https://www.mouser.fr/ProductDetail/TDK/B57442V5103J062?qs=xhbEVWpZdWcRenkX1j5YRA%3D%3D | 0.361 | 0 | 3 | 1.083
2 | D1, D2 | Diode | LED | 805 | LED CMS | CMD17-21VRC/TR8 | https://www.mouser.fr/ProductDetail/VCC/CMD17-21VRC-TR8?qs=sGAEpiMZZMv0DJfhVcWlK8AiAHwfAGPKl02p24KiHvY%3D | 0.473 | 0 | 6 | 2.838
1 | J1 | Connecteur | USB4135-GF-A | THT/SMD | Port USB-C 6 broches (Power Only) GCT ou équivalent | USB4135-GF-A | https://www.mouser.fr/ProductDetail/GCT/USB4135-GF-A?qs=Li%252BoUPsLEnt6HRo6RUvaXA%3D%3D | 0.585 | 0 | 3 | 1.755

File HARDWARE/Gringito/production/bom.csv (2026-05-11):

Designator | Footprint | Quantity | Value | LCSC Part #
_15, _14, _13, _12, _11, _10, _9, _8, _7, _6, _5, _4, _3, _2, |  | 15
C1, C20, C36, C42 | 0805 | 4 | 0,01u
C10, C15, C22, C26, C27, C3, C30, C31, C33, C35, C4, C8 | 0805 | 12 | 1u
C11, C16, C18, C19, C21, C23, C24, C28, C5, C6 | 0805 | 10 | 0,1u
C12 | 0805 | 1 | 4,7n
C13, C2, C25, C29 | 0805 | 4 | 10u
C14, C9 | 0805 | 2 | 4,7u
C17 | 0805 | 1 | 4700p
C32, C44 | 0805 | 2 | 22n
C34, C43 | 0805 | 2 | 0,47u
C37, C38, C39, C40, C41 | 0805 | 5 | TDB
C7 | 0805 | 1 | 33p
D1, D2 | 0805 | 2 | LED
J1 | USB_C_Receptacle_GCT_USB4135-GF-A_6P_TopMnt_Horizontal | 1 | USB_C_Receptacle_PowerOnly_6P
J2, J3, J4 | PinHeader_1x02_P2.54mm_Vertical | 3 | Conn_01x02
L1, L2 | SolderWire-1.5sqmm_1x02_P6mm_D1.7mm_OD3mm | 2 | L
R1 | 0805 | 1 | 1K
R10, R5 | 0805 | 2 | 10R
R11 | 0805 | 1 | 100K
R12 | 0805 | 1 | 76K8
R13, R15, R18, R19 | 0805 | 4 | 56,2K
R14, R16, R23, R27, R8 | 0805 | 5 | 10K
R17 | 0805 | 1 | NTC
R2, R4 | 0805 | 2 | 1R
R20 | 0805 | 1 | 56K2
R21, R22 | 0805 | 2 | 3,6K
R24 | 0805 | 1 | 470
R25 | 0805 | 1 | 470R
R26 | 0805 | 1 | 140R
R28 | 0805 | 1 | 360R
R29 | 0805 | 1 | 33K
R3 | 0805 | 1 | 20m
R6, R7 | 0805 | 2 | 5K1
R9 | 0805 | 1 | 12k1
U1, U8 | DBV0005A-IPC_A | 2 | PTPS7A2033PDBVR
U2 | DCK0006A_N | 1 | INA199A1DCKR
U3, U5 | DPC0008A | 2 | CSD97376Q4M
U4 | RGZ0048A | 1 | BQ500212ARGZR
U6 | RHL20_2P05X3P05 | 1 | BQ51013BRHLR
U7 | SOT-23-5_MC_MCH | 1 | MCP73831T-2ATI/OT

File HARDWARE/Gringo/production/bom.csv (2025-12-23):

Designator | Footprint | Quantity | Value | LCSC Part #
_21, _20, _19, _18, _17, _16, _15, _14, _13, _12, _11, _10, _9, _8, _7, _6, _5, _4, _3, _2, |  | 21
C1, C3 | 0603 | 2 | 10u
C2 | 0603 | 1 | 100n
C4 | 0603 | 1 | 22u
C5, C6, C7, C8 | 0603 | 4 | 1u
J1, J10, J11, J12, J2, J3, J5, J6, J7, J8, J9 | PinHeader_1x06_P2.54mm_Vertical | 11 | Conn_01x06
J13 | PinHeader_1x05_P2.54mm_Vertical | 1 | Conn_01x05_Pin
J4 | PinHeader_1x06_P2.54mm_Vertical | 1 | Alim
L1 | L_APV_ANR4030 | 1 | 2u2
R1, R2, R3, R6, R7 | 0603 | 5 | 4K7
R4 | 0603 | 1 | 750K
R5 | 0603 | 1 | 100K
U1 | RHL20_2P05X3P05 | 1 | BQ51013ARHLR
U2 | RGZ0048A | 1 | BQ500212ARGZT
U3 | SOT-23-5_MC_MCH | 1 | MCP73831T-2ACI/OT
U4, U6 | DBV0005A-IPC_A | 2 | PTPS7A2018PDBVR
U5 | 21-1048_F143A5&plus_1_MXM | 1 | MAX30101EFD+
U7 | SON12_U-DFN3030-12_DIO-M | 1 | PAM2401YPADJ
U8 | 21-100264_T2433&plus_2C_MXM | 1 | MAX32664GTGA+T
Y1 | XTAL_ECX-12_2X1P2_ECS | 1 | 32k768

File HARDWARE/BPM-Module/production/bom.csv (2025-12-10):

Designator | Footprint | Quantity | Value | LCSC Part #
C1, C7 | 0603 | 2 | 10u
C2 | 0603 | 1 | 100n
C3, C4, C5 | 0603 | 3 | 1u
C6 | 0603 | 1 | 22u
J1 | PinHeader_1x05_P2.54mm_Vertical | 1 | Conn_01x05_Pin
L1 | 0603 | 1 | 2u2
R1, R2, R3, R6, R7 | 0603 | 5 | 4K7
R4 | 0603 | 1 | 750K
R5 | 0603 | 1 | 100K
U1 | 21-1048_F143A5&plus_1_MXM-M | 1 | MAX30101EFD+
U2 | 21-100241A_W161K1&plus_1_MXM | 1 | MAX32664GWEA+T
U3 | SON12_U-DFN3030-12_DIO-M | 1 | PAM2401YPADJ
U4 | DBV0005A-IPC_A | 1 | PTPS7A2018PDBVR
Y1 | Crystal_SMD_2012-2Pin_2.0x1.2mm | 1 | 32k768

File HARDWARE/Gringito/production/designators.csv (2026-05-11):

:15
C1:1
C10:1
C11:1
C12:1
C13:1
C14:1
C15:1
C16:1
C17:1
C18:1
C19:1
C2:1
C20:1
C21:1
C22:1
C23:1
C24:1
C25:1
C26:1
C27:1
C28:1
C29:1
C3:1
C30:1
C31:1
C32:1
C33:1
C34:1
C35:1
C36:1
C37:1
C38:1
C39:1
C4:1
C40:1
C41:1
C42:1
C43:1
C44:1
C5:1
C6:1
C7:1
C8:1
C9:1
D1:1
D2:1
G***:1
J1:1
J2:1
J3:1
J4:1
L1:1
L2:1
NT1:1
R1:1
R10:1
R11:1
R12:1
R13:1
R14:1
R15:1
R16:1
R17:1
R18:1
R19:1
R2:1
R20:1
R21:1
R22:1
R23:1
R24:1
R25:1
R26:1
R27:1
R28:1
R29:1
R3:1
R4:1
R5:1
R6:1
R7:1
R8:1
R9:1
U1:1
U2:1
U3:1
U4:1
U5:1
U6:1
U7:1
U8:1

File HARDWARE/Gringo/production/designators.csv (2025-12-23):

:21
C1:1
C2:1
C3:1
C4:1
C5:1
C6:1
C7:1
C8:1
J1:1
J10:1
J11:1
J12:1
J13:1
J2:1
J3:1
J4:1
J5:1
J6:1
J7:1
J8:1
J9:1
L1:1
R1:1
R2:1
R3:1
R4:1
R5:1
R6:1
R7:1
REF**:3
U1:1
U2:1
U3:1
U4:1
U5:1
U6:1
U7:1
U8:1
Y1:1

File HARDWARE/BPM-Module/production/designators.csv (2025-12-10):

C1:1
C2:1
C3:1
C4:1
C5:1
C6:1
C7:1
J1:1
L1:1
R1:1
R2:1
R3:1
R4:1
R5:1
R6:1
R7:1
U1:1
U2:1
U3:1
U4:1
Y1:1

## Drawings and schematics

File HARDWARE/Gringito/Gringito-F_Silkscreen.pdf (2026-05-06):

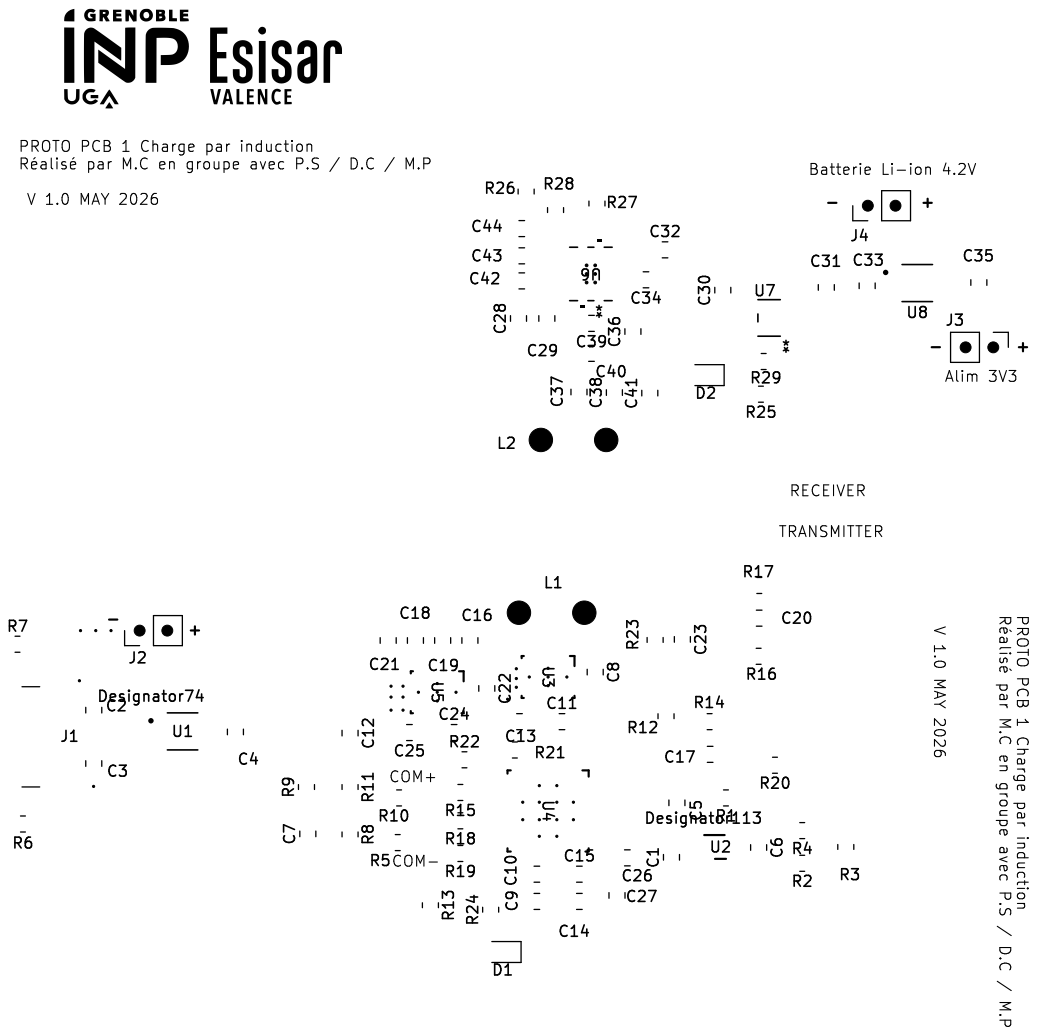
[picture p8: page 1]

PROTO PCB 1 Charge par induction
þÿRéalisé par M.C en groupe avec P.S / D.C / M.P

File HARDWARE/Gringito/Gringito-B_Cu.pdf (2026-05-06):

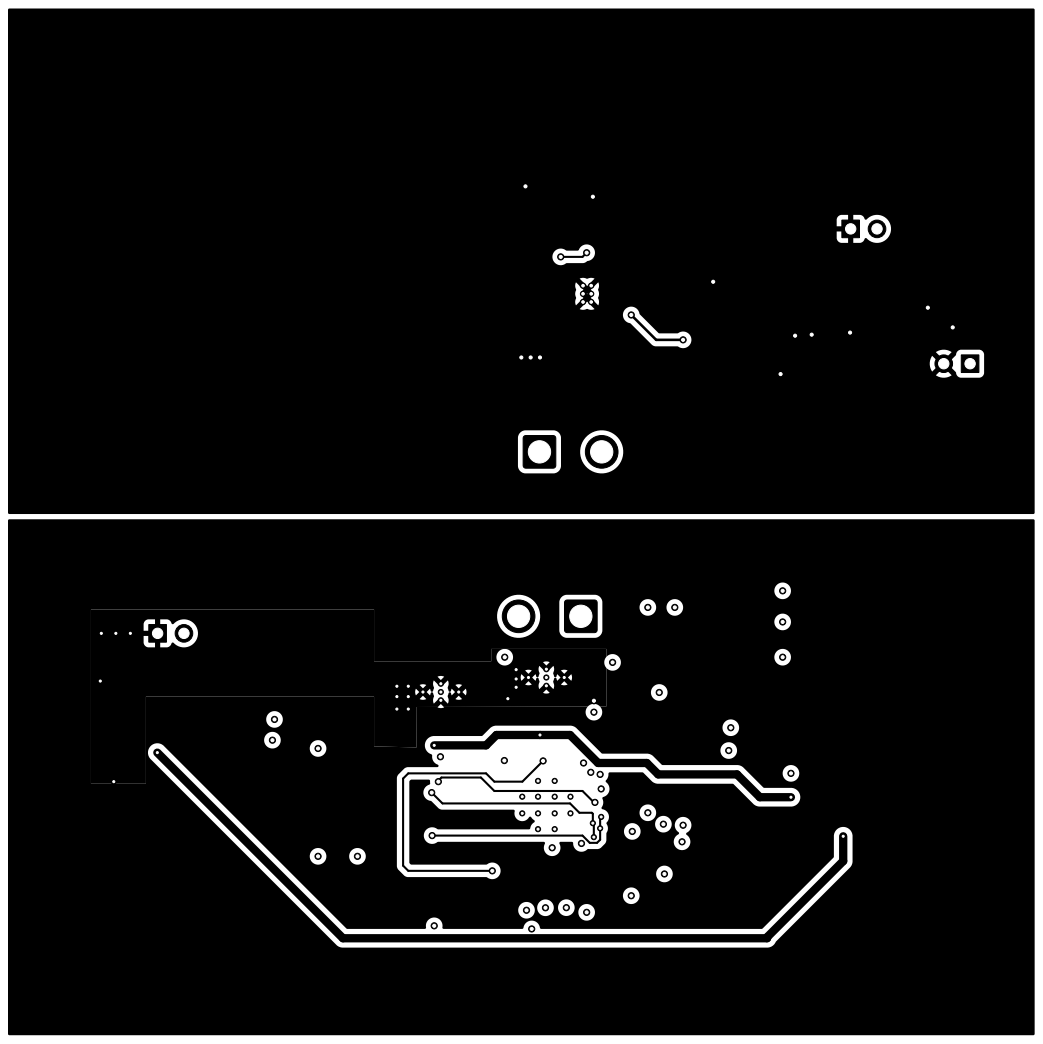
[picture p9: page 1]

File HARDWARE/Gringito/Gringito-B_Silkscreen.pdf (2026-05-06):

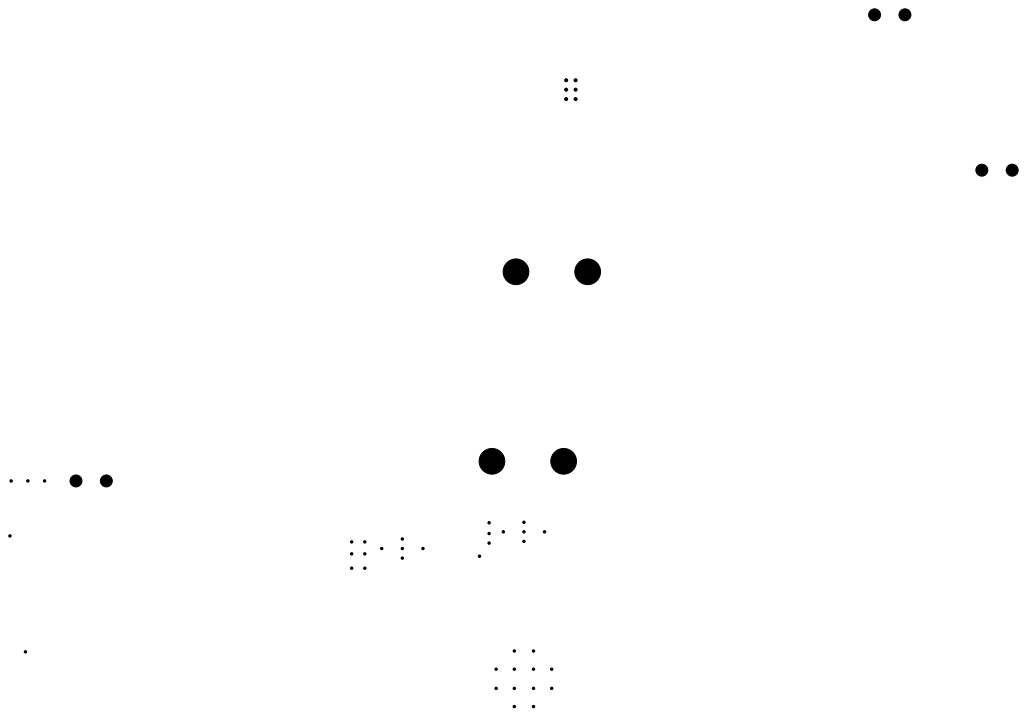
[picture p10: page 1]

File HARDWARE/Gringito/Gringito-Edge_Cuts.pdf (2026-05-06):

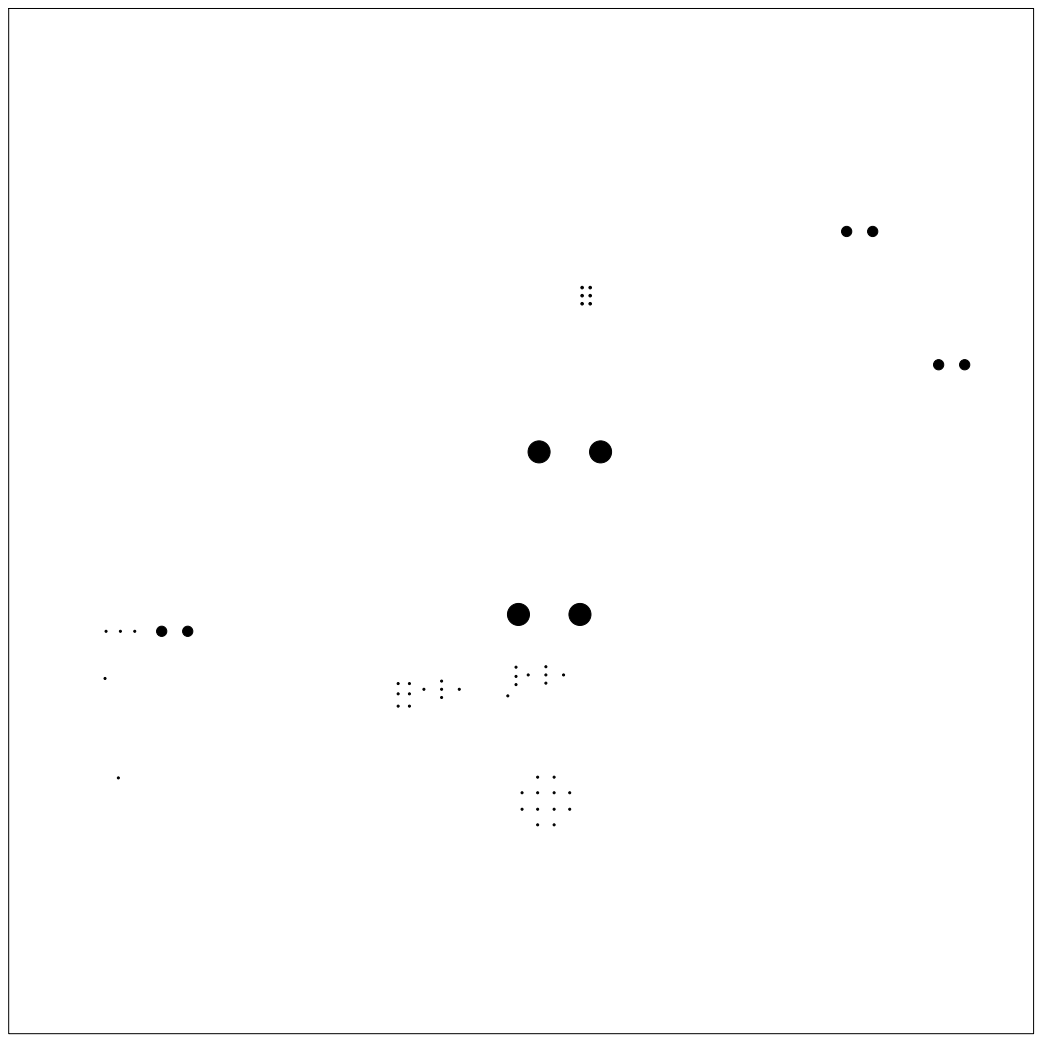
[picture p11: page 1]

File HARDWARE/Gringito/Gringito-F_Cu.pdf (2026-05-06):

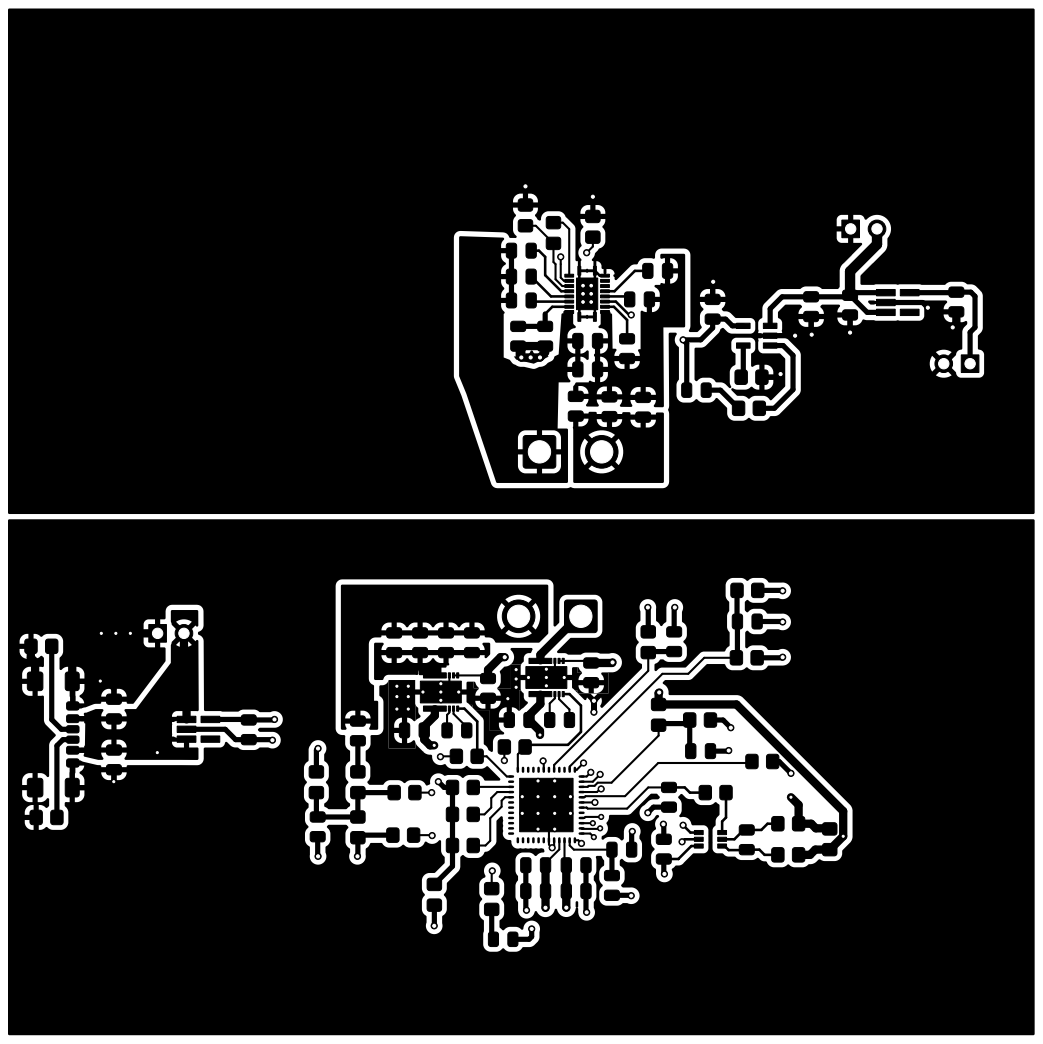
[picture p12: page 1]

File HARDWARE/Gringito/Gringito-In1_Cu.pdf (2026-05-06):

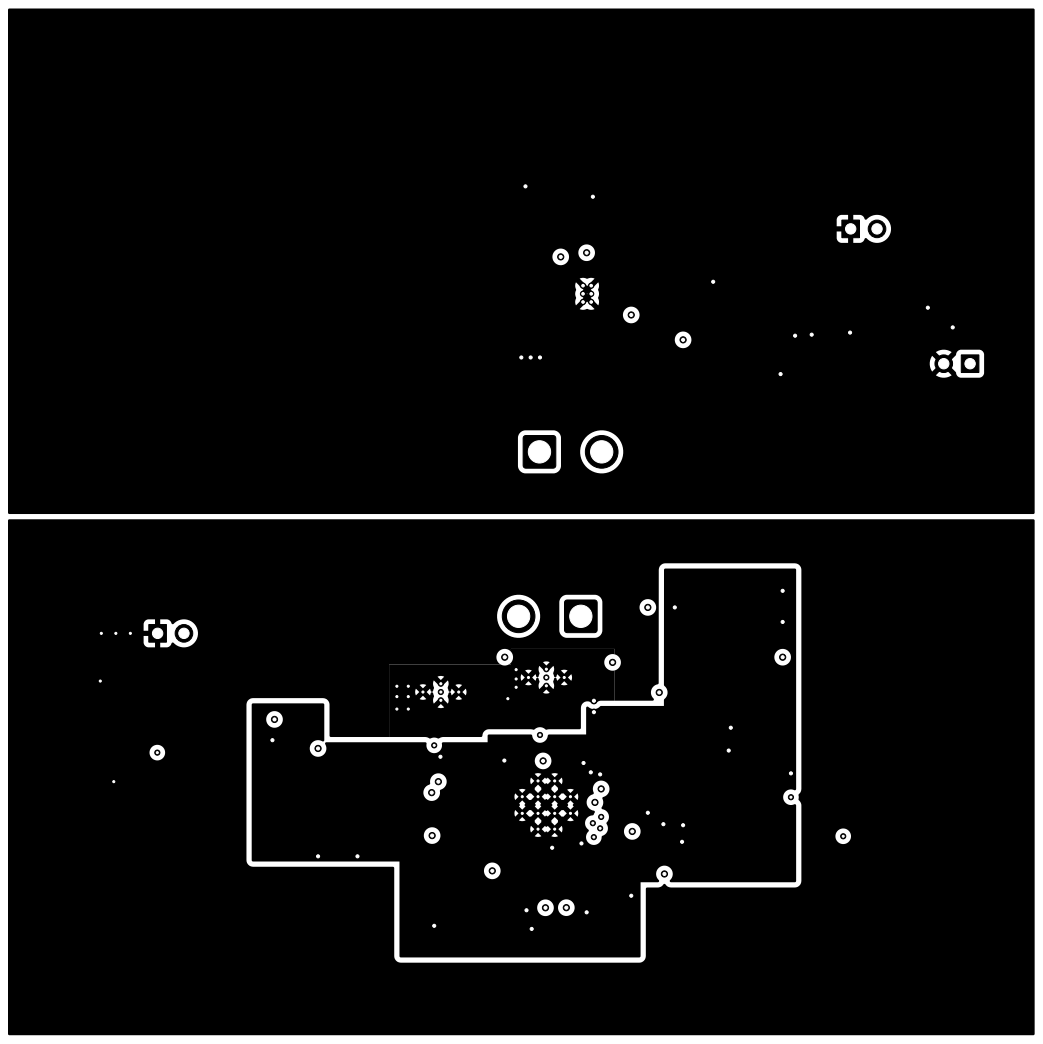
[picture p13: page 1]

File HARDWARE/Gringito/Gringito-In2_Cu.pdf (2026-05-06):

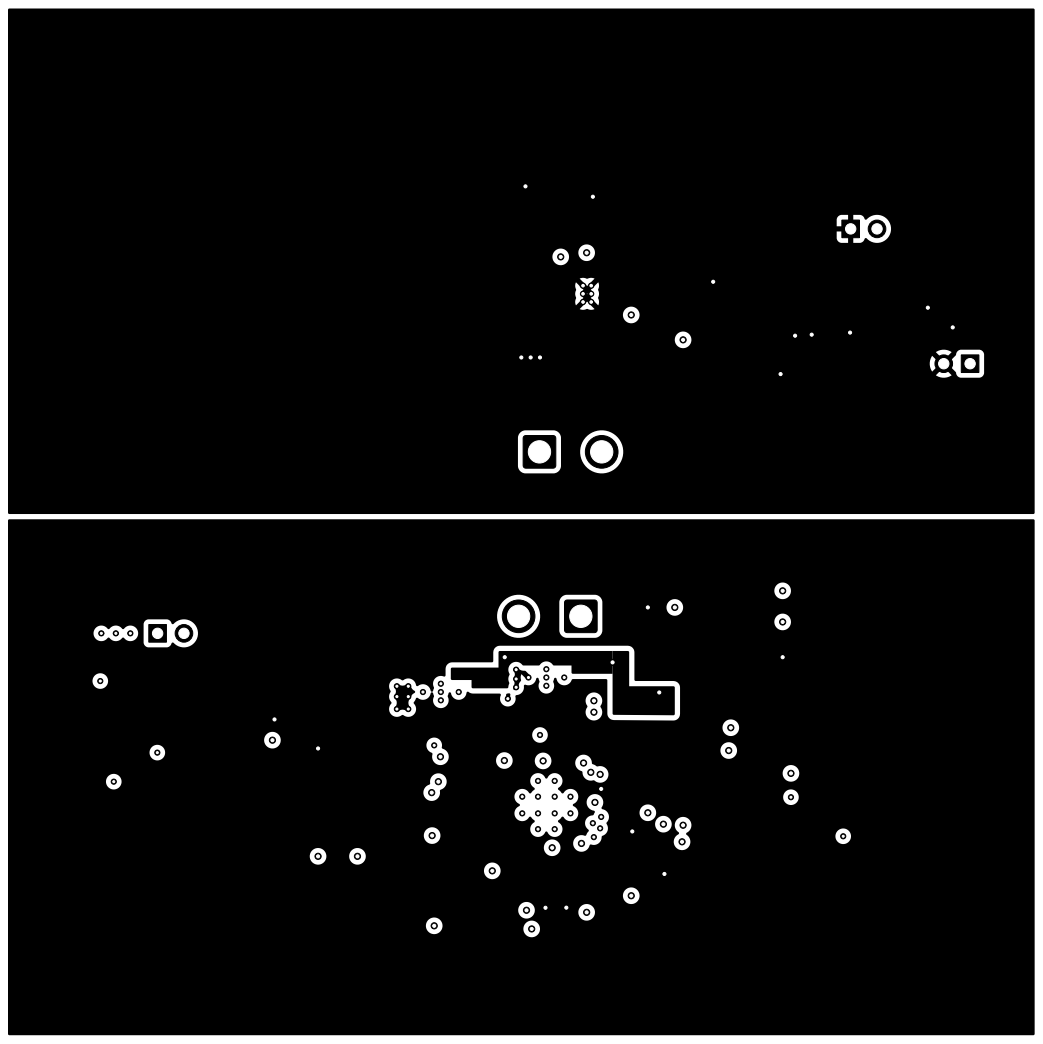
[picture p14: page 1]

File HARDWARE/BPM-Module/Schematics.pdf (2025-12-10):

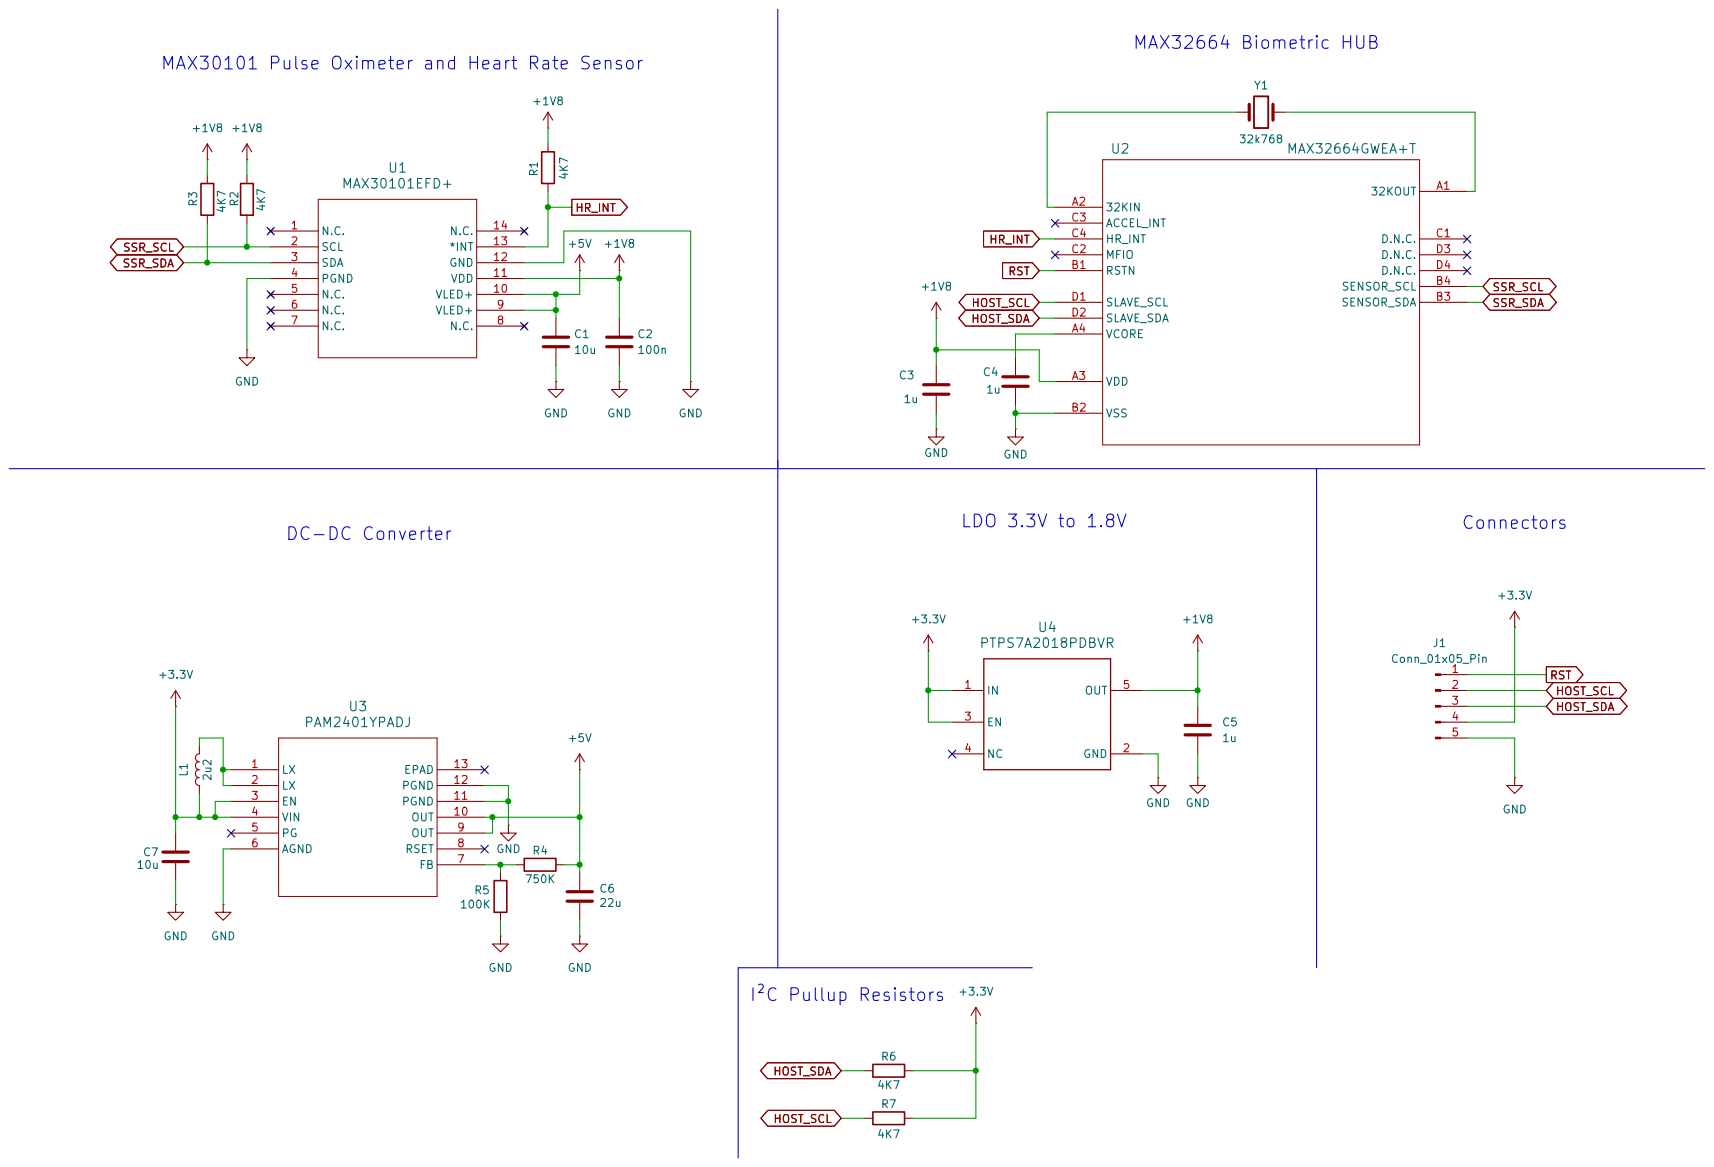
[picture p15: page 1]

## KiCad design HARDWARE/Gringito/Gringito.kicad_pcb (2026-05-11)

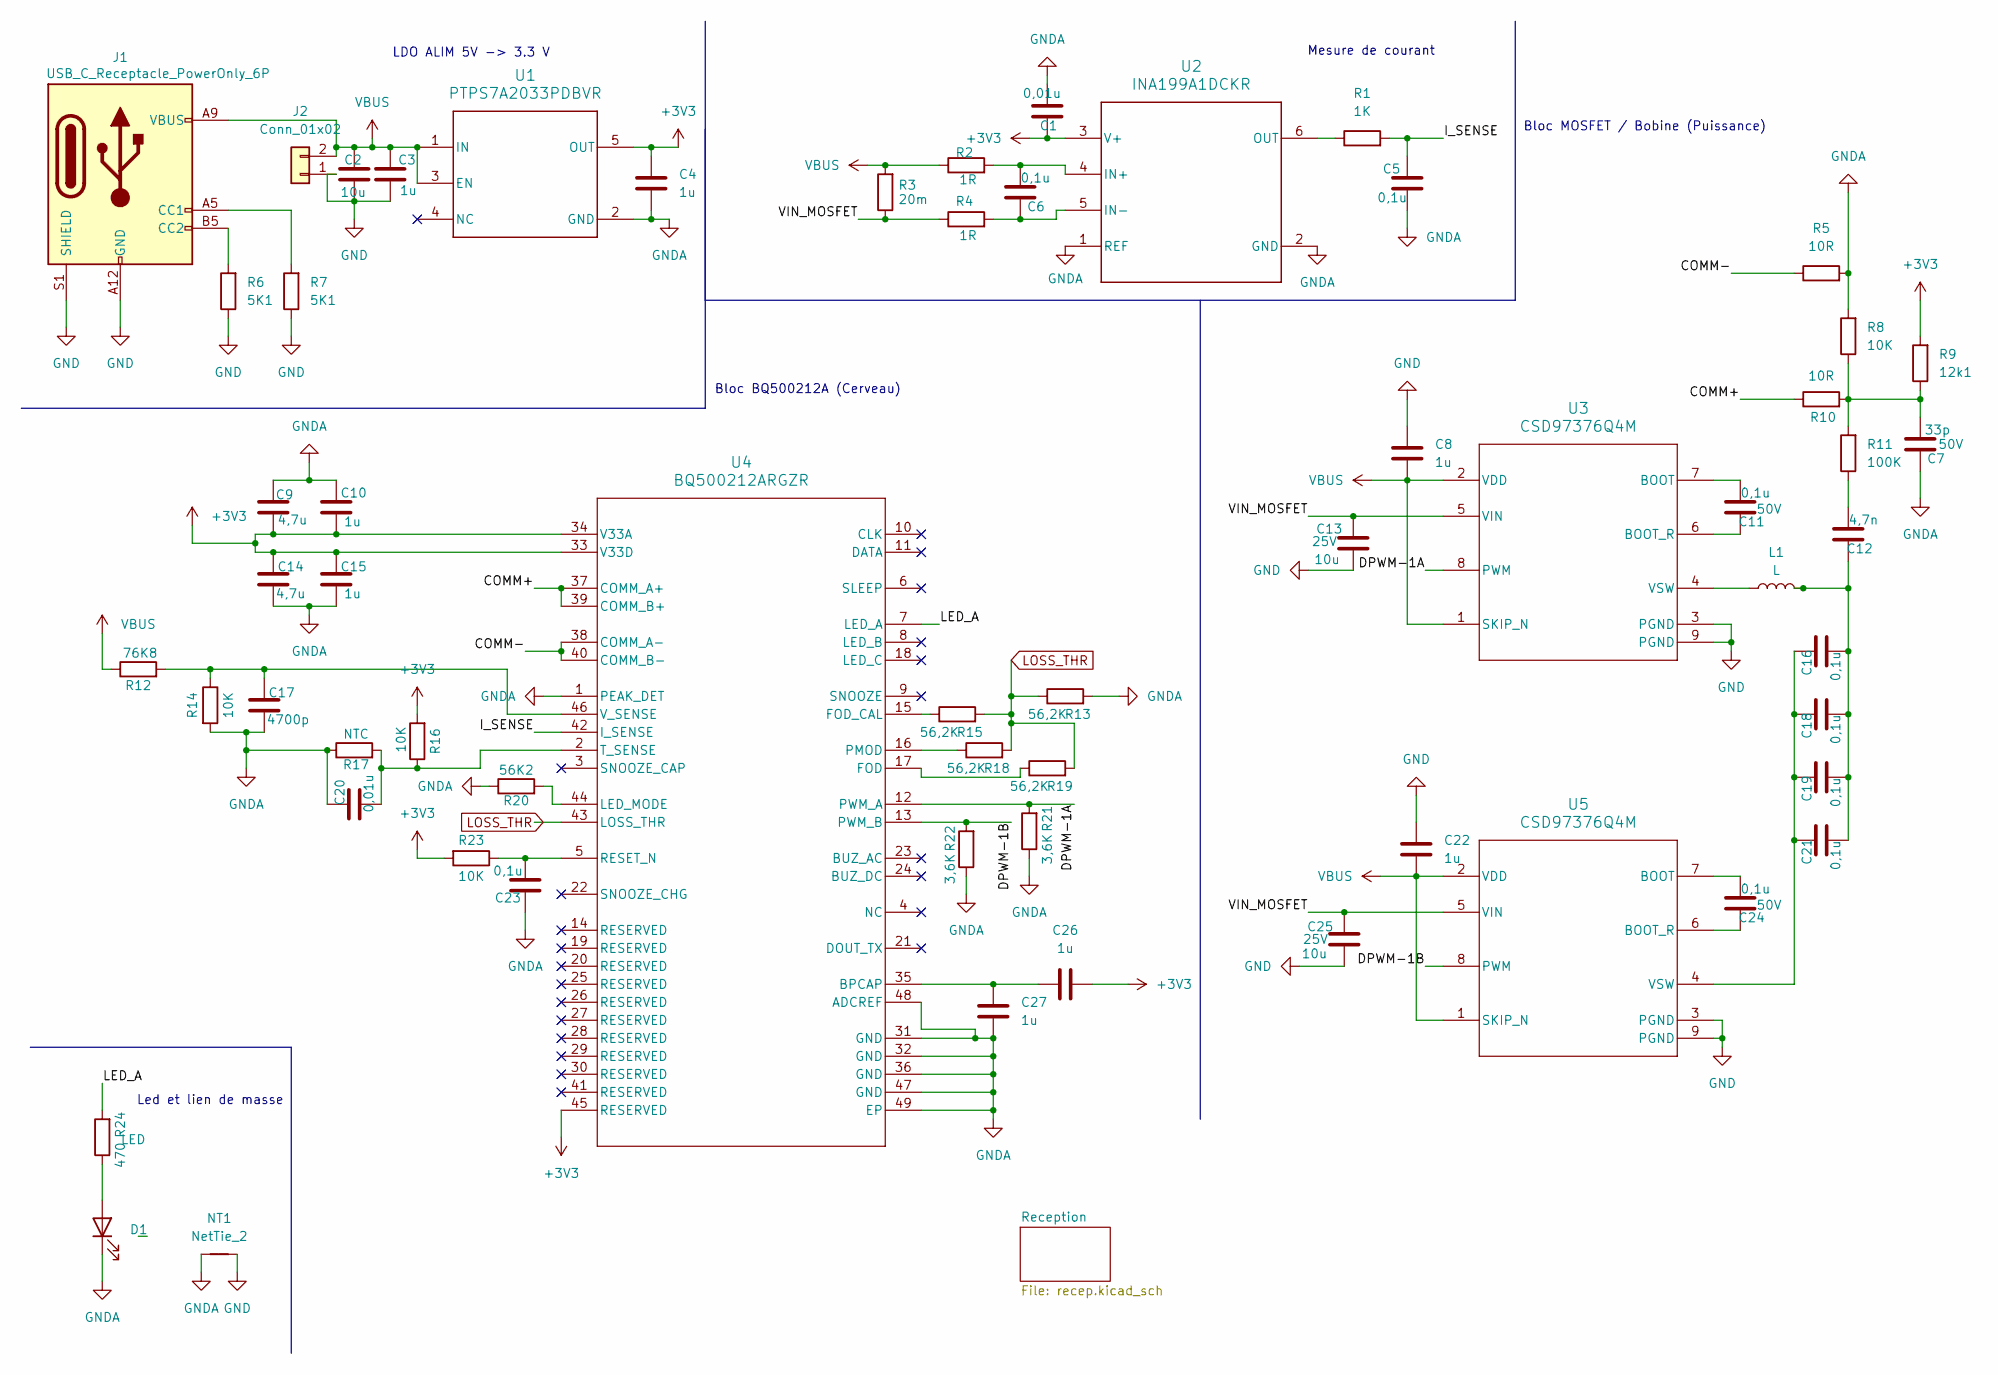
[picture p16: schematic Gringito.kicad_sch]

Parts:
C1, C20: 0,01u; C_0805_2012Metric
C2: 10u; C_0805_2012Metric
C3, C4, C8, C10, C15, C22, C26, C27: 1u; C_0805_2012Metric
C5, C6, C23: 0,1u; C_0805_2012Metric
C7: 33p; C_0805_2012Metric; voltage 50V
C9, C14: 4,7u; C_0805_2012Metric
C11, C24: 0,1u; C_0805_2012Metric; voltage 50V
C12: 4,7n; C_0805_2012Metric
C13: 10u; C_0805_2012Metric; Voltage 25V
C16, C18, C19, C21: 0,1u; C_1206_3216Metric_Pad1.33x1.80mm_HandSolder
C17: 4700p; C_0805_2012Metric
C25: 10u; C_0805_2012Metric; voltage 25V
D1: LED; LED_0805_2012Metric
J1: USB_C_Receptacle_PowerOnly_6P; USB_C_Receptacle_GCT_USB4135-GF-A_6P_TopMnt_Horizontal
J2: Conn_01x02; PinHeader_1x02_P2.54mm_Vertical
L1: L; SolderWire-1.5sqmm_1x02_P6mm_D1.7mm_OD3mm
NT1: NetTie_2; NetTie-2_SMD_Pad0.5mm
R1: 1K; R_0805_2012Metric_Pad1.20x1.40mm_HandSolder
R2, R4: 1R; R_0805_2012Metric_Pad1.20x1.40mm_HandSolder
R3: 20m; R_0805_2012Metric_Pad1.20x1.40mm_HandSolder
R5, R10: 10R; R_0805_2012Metric_Pad1.20x1.40mm_HandSolder
R6, R7: 5K1; R_0805_2012Metric_Pad1.20x1.40mm_HandSolder
R8, R14, R16, R23: 10K; R_0805_2012Metric_Pad1.20x1.40mm_HandSolder
R9: 12k1; R_0805_2012Metric_Pad1.20x1.40mm_HandSolder
R11: 100K; R_0805_2012Metric_Pad1.20x1.40mm_HandSolder
R12: 76K8; R_0805_2012Metric_Pad1.20x1.40mm_HandSolder
R13, R15, R18, R19: 56,2K; R_0805_2012Metric_Pad1.20x1.40mm_HandSolder
R17: NTC; R_0805_2012Metric_Pad1.20x1.40mm_HandSolder
R20: 56K2; R_0805_2012Metric_Pad1.20x1.40mm_HandSolder
R21, R22: 3,6K; R_0805_2012Metric_Pad1.20x1.40mm_HandSolder
R24: 470; R_0805_2012Metric_Pad1.20x1.40mm_HandSolder
U1: PTPS7A2033PDBVR; DBV0005A-IPC_A
U2: INA199A1DCKR; DCK0006A_N
U3, U5: CSD97376Q4M; DPC0008A
U4: BQ500212ARGZR; RGZ0048A

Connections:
+3V3: C1.1, C4.1, C9.2, C10.2, C14.1, C15.1, C26.1, R9.2, R16.2, R23.2, U1.5 (OUT), U2.3 (V+), U4.33 (V33D), U4.34 (V33A), U4.45 (RESERVED)
/COMM+: R10.1, U4.37 (COMM_A+), U4.39 (COMM_B+)
/COMM-: R5.1, U4.38 (COMM_A-), U4.40 (COMM_B-)
/DPWM-1A: R21.2, U3.8 (PWM), U4.12 (PWM_A)
/DPWM-1B: R22.2, U4.13 (PWM_B), U5.8 (PWM)
/I_SENSE: C5.1, R1.2, U4.42 (I_SENSE)
/LED_A: R24.2, U4.7 (LED_A)
/VIN_MOSFET: C13.1, C25.1, R3.1, R4.1, U3.5 (VIN), U5.5 (VIN)
GND: C2.2, C3.2, C8.2, C13.2, C22.2, C25.2, J1.A12 (GND), J1.B12 (GND), J1.S1 (SHIELD), J2.1, NT1.2, R6.1, R7.1, U3.3 (PGND), U3.9 (PGND), U3.V, U5.3 (PGND), U5.9 (PGND), U5.V
GNDA: C1.2, C4.2, C5.2, C7.1, C9.1, C10.1, C14.2, C15.2, C17.2, C20.1, C23.1, C27.1, D1.1 (K), NT1.1, R5.2, R8.2, R13.2, R14.2, R17.1, R20.1, R21.1, R22.1, U1.2 (GND), U2.1 (REF), U2.2 (GND), U4.1 (PEAK_DET), U4.31 (GND), U4.32 (GND), U4.36 (GND), U4.47 (GND), U4.48 (ADCREF), U4.49 (EP), U4.V
LOSS_THR: R13.1, R15.2, R18.2, R19.2, U4.43 (LOSS_THR)
unnamed: C7.2, R8.1, R9.1, R10.2, R11.2
unnamed: C12.1, C16.2, C18.2, C19.2, C21.2, L1.2
unnamed: C12.2, R11.1
unnamed: D1.2 (A), R24.1
unnamed: J1.A5 (CC1), R7.2
unnamed: J1.B5 (CC2), R6.2
unnamed: C6.2, R2.2, U2.4 (IN+)
unnamed: C6.1, R4.2, U2.5 (IN-)
unnamed: R1.1, U2.6 (OUT)
unnamed: C11.2, U3.7 (BOOT)
unnamed: C11.1, U3.6 (BOOT_R)
unnamed: L1.1, U3.4 (VSW)
unnamed: C26.2, C27.2, U4.35 (BPCAP)
unnamed: R19.1, U4.17 (FOD)
unnamed: R15.1, U4.15 (FOD_CAL)
unnamed: R20.2, U4.44 (LED_MODE)
unnamed: R18.1, U4.16 (PMOD)
unnamed: C23.2, R23.1, U4.5 (RESET_N)
unnamed: C20.2, R16.1, R17.2, U4.2 (T_SENSE)
unnamed: C17.1, R12.2, R14.1, U4.46 (V_SENSE)
unnamed: C24.2, U5.7 (BOOT)
unnamed: C24.1, U5.6 (BOOT_R)
unnamed: C16.1, C18.1, C19.1, C21.1, U5.4 (VSW)
VBUS: C2.1, C3.1, C8.1, C22.1, J1.A9 (VBUS), J1.B9 (VBUS), J2.2, R2.1, R3.2, R12.1, U1.1 (IN), U1.3 (EN), U3.1 (SKIP_N), U3.2 (VDD), U5.1 (SKIP_N), U5.2 (VDD)

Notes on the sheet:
Bloc BQ500212A (Cerveau)
Led et lien de masse
Bloc MOSFET / Bobine (Puissance)
LDO ALIM 5V -> 3.3 V
Mesure de courant

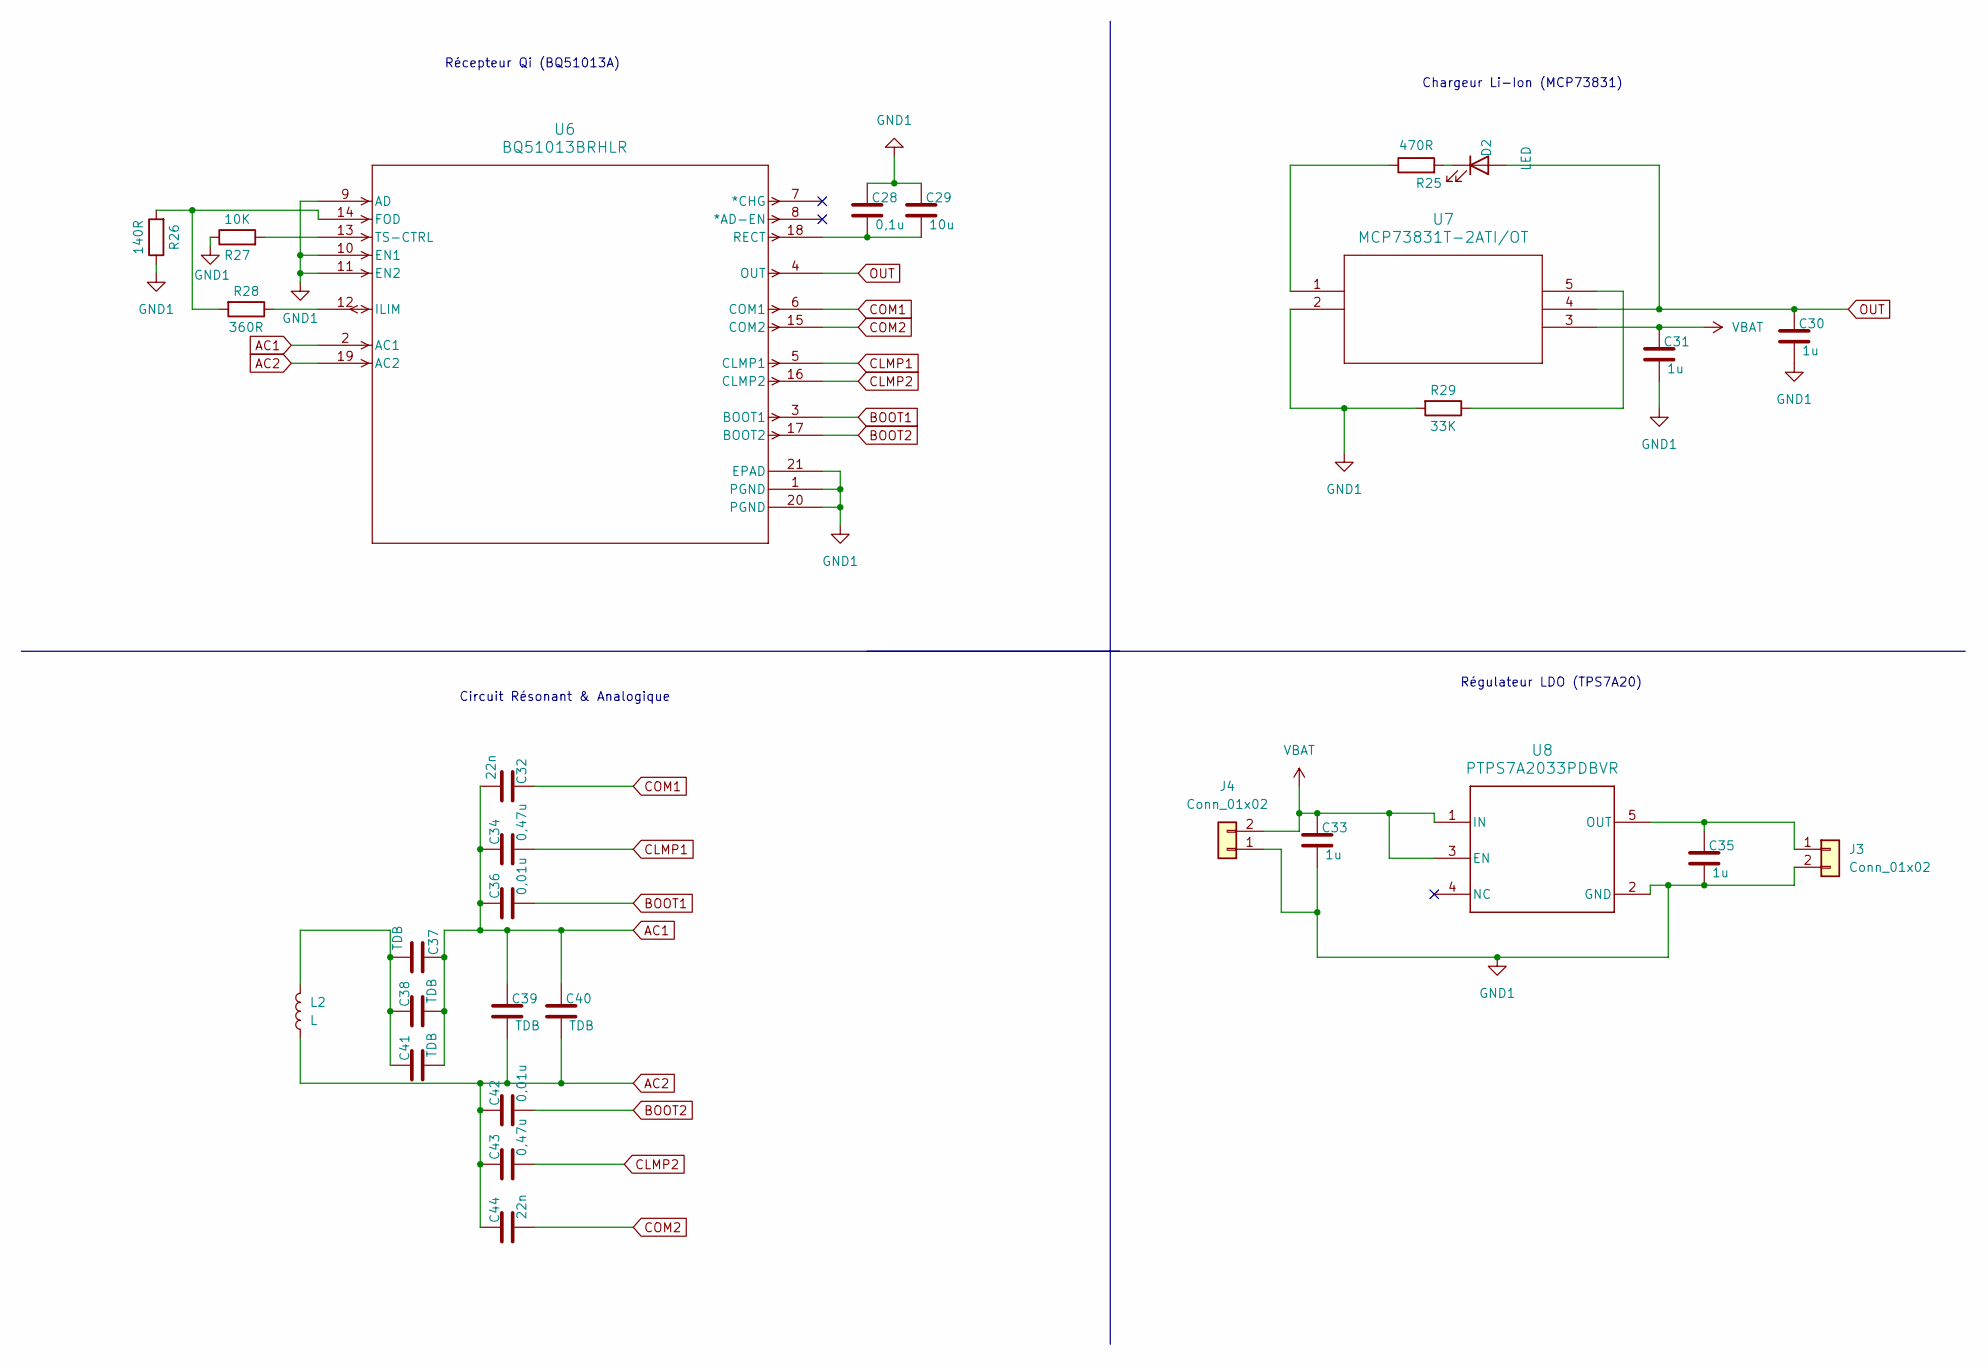
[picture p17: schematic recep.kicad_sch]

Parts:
C28: 0,1u; C_0805_2012Metric
C29: 10u; C_0805_2012Metric
C30, C31, C33, C35: 1u; C_0805_2012Metric
C32, C44: 22n; C_0805_2012Metric
C34, C43: 0,47u; C_0805_2012Metric
C36, C42: 0,01u; C_0805_2012Metric
C37, C38, C39, C40, C41: TDB; C_0805_2012Metric
D2: LED; LED_0805_2012Metric
J3, J4: Conn_01x02; PinHeader_1x02_P2.54mm_Vertical
L2: L; SolderWire-1.5sqmm_1x02_P6mm_D1.7mm_OD3mm
R25: 470R; R_0805_2012Metric_Pad1.20x1.40mm_HandSolder
R26: 140R; R_0805_2012Metric_Pad1.20x1.40mm_HandSolder
R27: 10K; R_0805_2012Metric_Pad1.20x1.40mm_HandSolder
R28: 360R; R_0805_2012Metric_Pad1.20x1.40mm_HandSolder
R29: 33K; R_0805_2012Metric_Pad1.20x1.40mm_HandSolder
U6: BQ51013BRHLR; RHL20_2P05X3P05
U7: MCP73831T-2ATI/OT; SOT-23-5_MC_MCH
U8: PTPS7A2033PDBVR; DBV0005A-IPC_A

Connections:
AC1: C32.2, C34.1, C36.1, C37.1, C38.2, C39.1, C40.1, C41.2, U6.2 (AC1)
AC2: C39.2, C40.2, C42.1, C43.1, C44.1, L2.1, U6.19 (AC2)
BOOT1: C36.2, U6.3 (BOOT1)
BOOT2: C42.2, U6.17 (BOOT2)
CLMP1: C34.2, U6.5 (CLMP1)
CLMP2: C43.2, U6.16 (CLMP2)
COM1: C32.1, U6.6 (COM1)
COM2: C44.2, U6.15 (COM2)
GND1: C28.1, C29.1, C30.2, C31.2, C33.2, C35.2, J3.2, J4.1, R26.1, R27.1, R29.2, U6.1 (PGND), U6.9 (AD), U6.10 (EN1), U6.11 (EN2), U6.20 (PGND), U6.21 (EPAD), U6.V, U7.2, U8.2 (GND)
unnamed: C37.2, C38.1, C41.1, L2.2
unnamed: D2.1 (K), R25.2
unnamed: C35.1, J3.1, U8.5 (OUT)
unnamed: R25.1, U7.1
unnamed: R29.1, U7.5
unnamed: R26.2, R28.2, U6.14 (FOD)
unnamed: R28.1, U6.12 (ILIM)
unnamed: C28.2, C29.2, U6.18 (RECT)
unnamed: R27.2, U6.13 (TS-CTRL)
OUT: C30.1, D2.2 (A), U6.4 (OUT), U7.4
VBAT: C31.1, C33.1, J4.2, U7.3, U8.1 (IN), U8.3 (EN)

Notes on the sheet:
Récepteur Qi (BQ51013A)
Chargeur Li-Ion (MCP73831)
Circuit Résonant & Analogique
Régulateur LDO (TPS7A20)

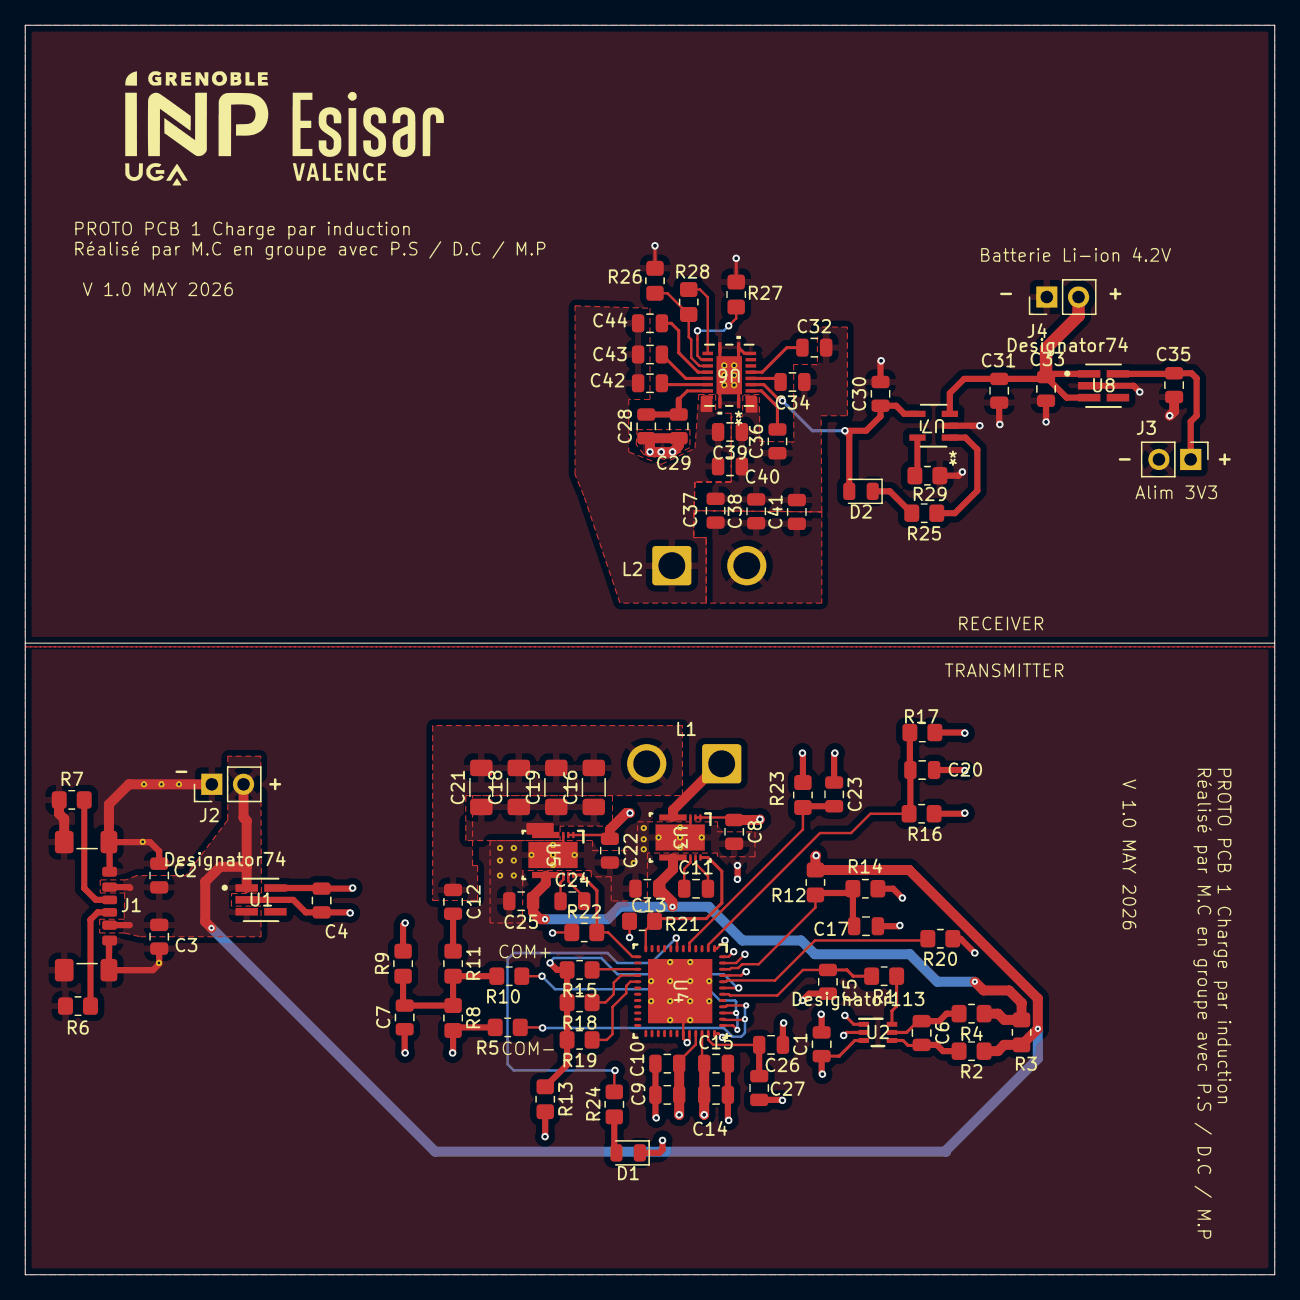
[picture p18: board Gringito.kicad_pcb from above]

Board: 4 copper layers, 100.0 x 100.0 mm, 90 parts (0 on the bottom side), 55 nets.

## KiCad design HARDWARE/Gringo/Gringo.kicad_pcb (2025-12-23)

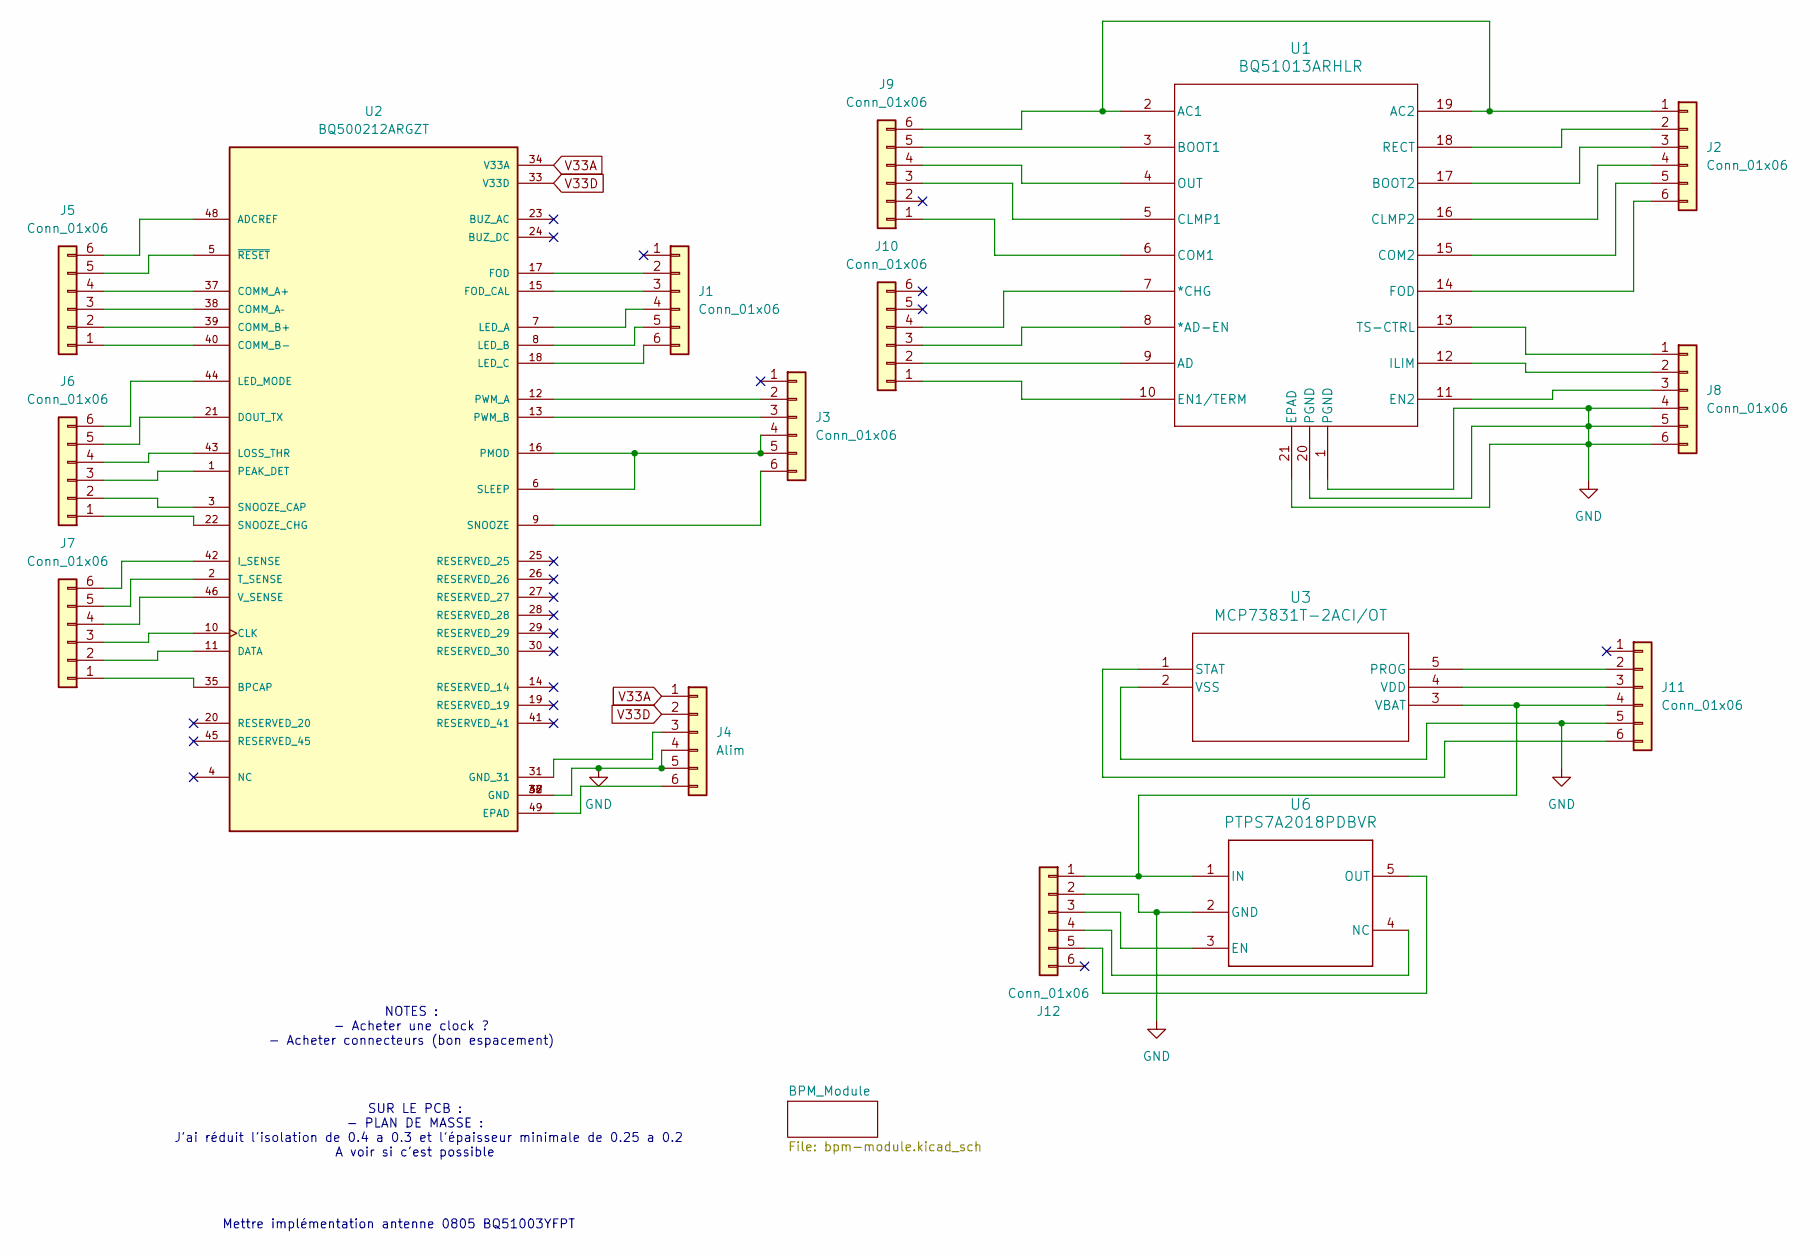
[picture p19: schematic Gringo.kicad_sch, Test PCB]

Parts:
J1, J2, J3, J5, J6, J7, J8, J9, J10, J11, J12: Conn_01x06; PinHeader_1x06_P2.54mm_Vertical
J4: Alim; PinHeader_1x06_P2.54mm_Vertical
U1: BQ51013ARHLR; RHL20_2P05X3P05
U2: BQ500212ARGZT; RGZ0048A; PARTREV D
U3: MCP73831T-2ACI/OT; SOT-23-5_MC_MCH
U6: PTPS7A2018PDBVR; DBV0005A-IPC_A

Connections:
GND: J4.4, J4.5, J8.4, J8.5, J8.6, J11.5, J12.2, U1.1 (PGND), U1.20 (PGND), U1.21 (EPAD), U2.32 (GND), U2.36 (GND), U2.47 (GND), U3.2 (VSS), U6.2 (GND); also elsewhere on the board
unnamed: J1.2, U2.17 (FOD)
unnamed: J1.3, U2.15 (FOD_CAL)
unnamed: J1.4, U2.7 (LED_A)
unnamed: J1.5, U2.8 (LED_B)
unnamed: J1.6, U2.18 (LED_C)
unnamed: J2.1, J9.6, U1.2 (AC1), U1.19 (AC2)
unnamed: J2.2, U1.18 (RECT)
unnamed: J2.3, U1.17 (BOOT2)
unnamed: J2.4, U1.16 (CLMP2)
unnamed: J2.5, U1.15 (COM2)
unnamed: J2.6, U1.14 (FOD)
unnamed: J3.2, U2.12 (PWM_A)
unnamed: J3.3, U2.13 (PWM_B)
unnamed: J3.4, J3.5, U2.6 (SLEEP), U2.16 (PMOD)
unnamed: J3.6, U2.9 (SNOOZE)
unnamed: J4.3, U2.31 (GND_31)
unnamed: J4.6, U2.49 (EPAD)
unnamed: J5.1, U2.40 (COMM_B-)
unnamed: J5.2, U2.39 (COMM_B+)
unnamed: J5.3, U2.38 (COMM_A–)
unnamed: J5.4, U2.37 (COMM_A+)
unnamed: J5.5, U2.5 (~RESET)
unnamed: J5.6, U2.48 (ADCREF)
unnamed: J6.1, U2.22 (SNOOZE_CHG)
unnamed: J6.2, U2.3 (SNOOZE_CAP)
unnamed: J6.3, U2.1 (PEAK_DET)
unnamed: J6.4, U2.43 (LOSS_THR)
unnamed: J6.5, U2.21 (DOUT_TX)
unnamed: J6.6, U2.44 (LED_MODE)
unnamed: J7.1, U2.35 (BPCAP)
unnamed: J7.2, U2.11 (DATA)
unnamed: J7.3, U2.10 (CLK)
unnamed: J7.4, U2.46 (V_SENSE)
unnamed: J7.5, U2.2 (T_SENSE)
unnamed: J7.6, U2.42 (I_SENSE)
unnamed: J8.1, U1.13 (TS-CTRL)
unnamed: J8.2, U1.12 (ILIM)
unnamed: J8.3, U1.11 (EN2)
unnamed: J9.1, U1.6 (COM1)
unnamed: J9.3, U1.5 (CLMP1)
unnamed: J9.4, U1.4 (OUT)
unnamed: J9.5, U1.3 (BOOT1)
unnamed: J10.1, U1.10 (EN1/TERM)
unnamed: J10.2, U1.9 (AD)
unnamed: J10.3, U1.8 (*AD-EN)
unnamed: J10.4, U1.7 (*CHG)
unnamed: J11.2, U3.5 (PROG)
unnamed: J11.3, U3.4 (VDD)
unnamed: J11.4, J12.1, U3.3 (VBAT), U6.1 (IN)
unnamed: J11.6, U3.1 (STAT)
unnamed: J12.3, U6.3 (EN)
unnamed: J12.4, U6.4 (NC)
unnamed: J12.5, U6.5 (OUT)
V33A: J4.1, U2.34 (V33A)
V33D: J4.2, U2.33 (V33D)

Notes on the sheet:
SUR LE PCB : - PLAN DE MASSE : J'ai réduit l'isolation de 0.4 a 0.3 et l'épaisseur minimale de 0.25 a 0.2 A voir si c'est possible
NOTES : - Acheter une clock ? - Acheter connecteurs (bon espacement)
Mettre implémentation antenne 0805 BQ51003YFPT

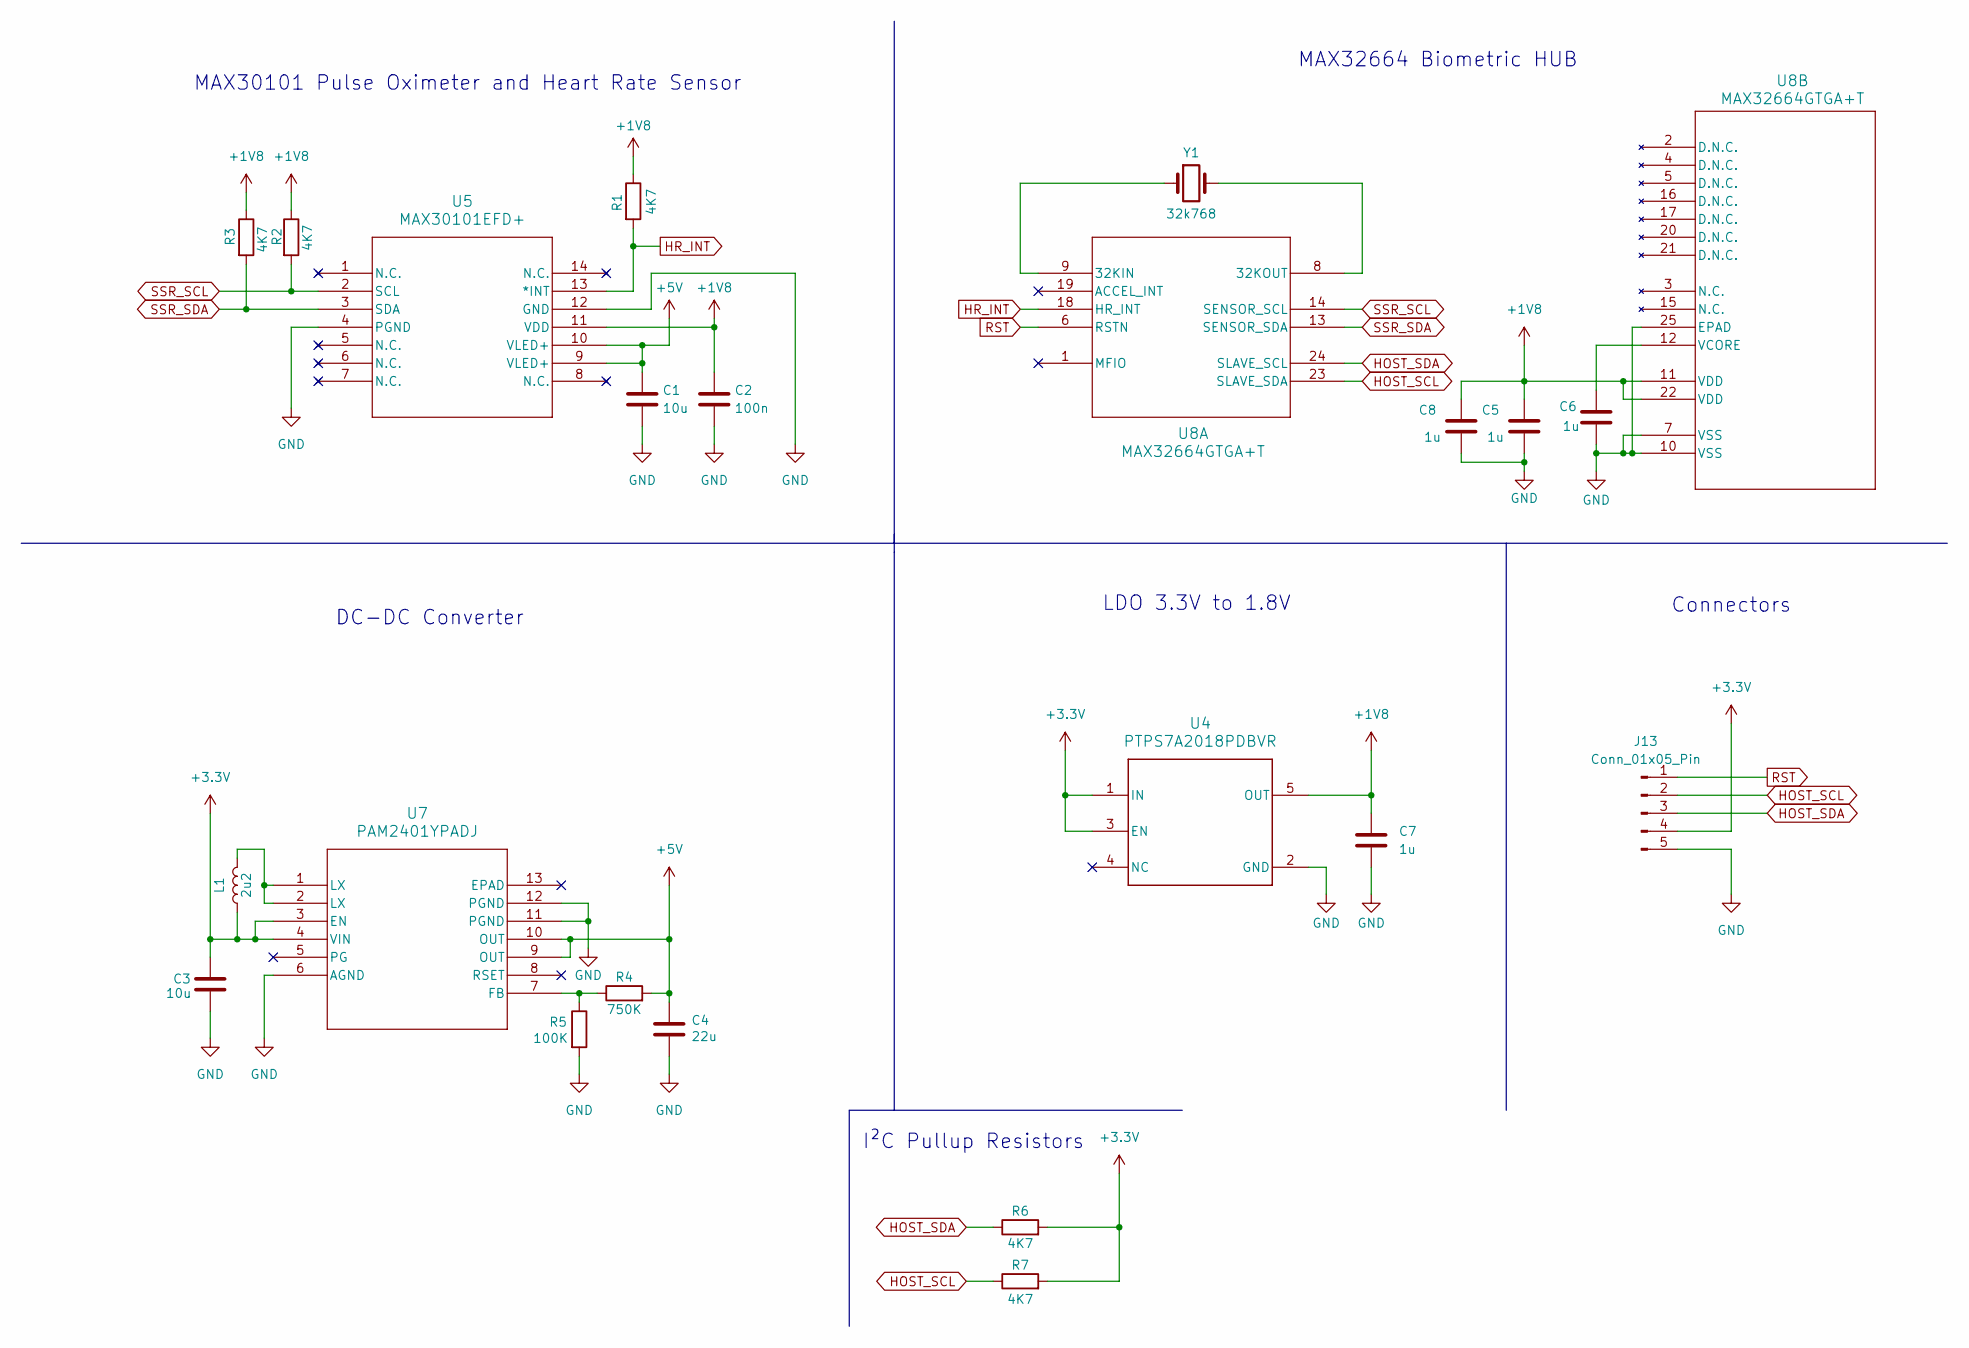
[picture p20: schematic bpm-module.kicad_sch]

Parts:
C1, C3: 10u; C_0603_1608Metric
C2: 100n; C_0603_1608Metric
C4: 22u; C_0603_1608Metric
C5, C6, C7, C8: 1u; C_0603_1608Metric
J13: Conn_01x05_Pin; PinHeader_1x05_P2.54mm_Vertical
L1: 2u2; L_APV_ANR4030
R1, R2, R3, R6, R7: 4K7; R_0603_1608Metric
R4: 750K; R_0603_1608Metric
R5: 100K; R_0603_1608Metric
U4: PTPS7A2018PDBVR; DBV0005A-IPC_A
U5: MAX30101EFD+; 21-1048_F143A5&plus_1_MXM
U7: PAM2401YPADJ; SON12_U-DFN3030-12_DIO-M
U8: MAX32664GTGA+T; 21-100264_T2433&plus_2C_MXM
Y1: 32k768; XTAL_ECX-12_2X1P2_ECS

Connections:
+1V8: C2.1, C5.1, C7.1, C8.1, R1.1, R2.1, R3.1, U4.5 (OUT), U5.11 (VDD), U8.11 (VDD), U8.22 (VDD)
+3.3V: C3.1, J13.4, L1.1, R6.2, R7.2, U4.1 (IN), U4.3 (EN), U7.3 (EN), U7.4 (VIN)
+5V: C1.1, C4.1, R4.2, U5.9 (VLED+), U5.10 (VLED+), U7.9 (OUT), U7.10 (OUT)
GND: C1.2, C2.2, C3.2, C4.2, C5.2, C6.2, C7.2, C8.2, J13.5, R5.2, U4.2 (GND), U5.4 (PGND), U5.12 (GND), U7.6 (AGND), U7.11 (PGND), U7.12 (PGND), U8.7 (VSS), U8.10 (VSS), U8.25 (EPAD); also elsewhere on the board
HOST_SCL: J13.2, R7.1, U8.23 (SLAVE_SDA)
HOST_SDA: J13.3, R6.1, U8.24 (SLAVE_SCL)
HR_INT: R1.2, U5.13 (*INT), U8.18 (HR_INT)
unnamed: L1.2, U7.1 (LX), U7.2 (LX)
unnamed: R4.1, R5.1, U7.7 (FB)
unnamed: U8.9 (32KIN), Y1.1
unnamed: U8.8 (32KOUT), Y1.2
unnamed: C6.1, U8.12 (VCORE)
RST: J13.1, U8.6 (RSTN)
SSR_SCL: R2.2, U5.2 (SCL), U8.14 (SENSOR_SCL)
SSR_SDA: R3.2, U5.3 (SDA), U8.13 (SENSOR_SDA)

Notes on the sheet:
Connectors
LDO 3.3V to 1.8V
I²C Pullup Resistors
MAX30101 Pulse Oximeter and Heart Rate Sensor
MAX32664 Biometric HUB
DC-DC Converter

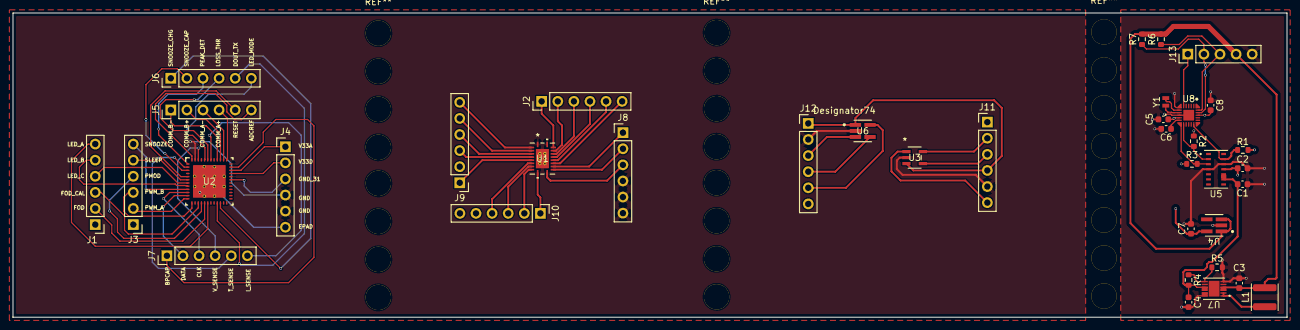
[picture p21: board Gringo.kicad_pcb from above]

Board: 2 copper layers, 201.0 x 48.0 mm, 38 parts (0 on the bottom side), 70 nets.

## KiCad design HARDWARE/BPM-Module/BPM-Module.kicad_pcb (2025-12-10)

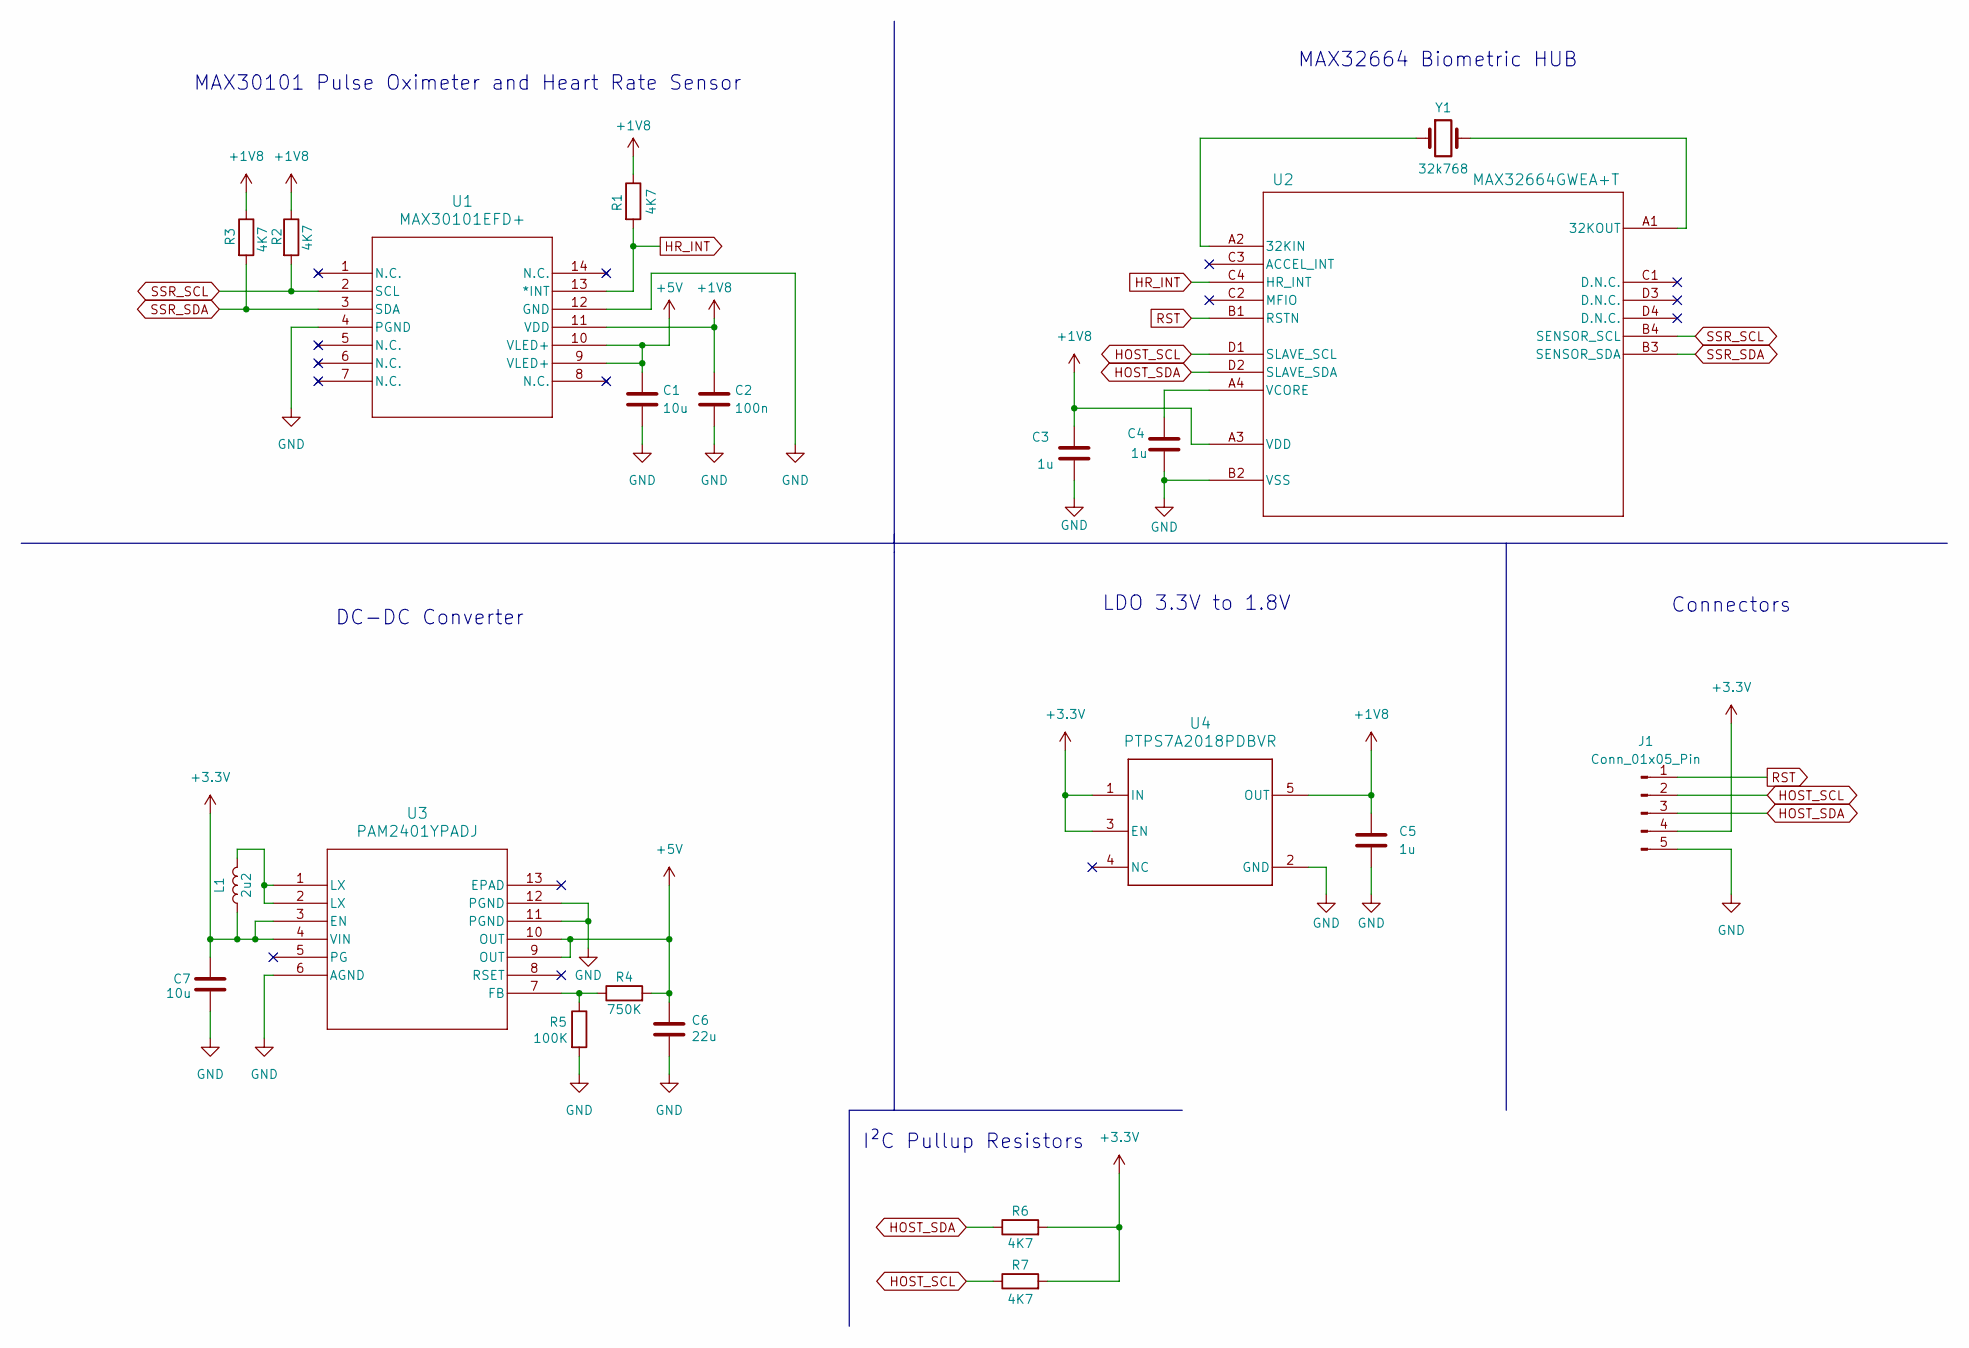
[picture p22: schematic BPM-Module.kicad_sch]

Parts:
C1, C7: 10u; C_0603_1608Metric
C2: 100n; C_0603_1608Metric
C3, C4, C5: 1u; C_0603_1608Metric
C6: 22u; C_0603_1608Metric
J1: Conn_01x05_Pin; PinHeader_1x05_P2.54mm_Vertical
L1: 2u2; L_0603_1608Metric
R1, R2, R3, R6, R7: 4K7; R_0603_1608Metric
R4: 750K; R_0603_1608Metric
R5: 100K; R_0603_1608Metric
U1: MAX30101EFD+; 21-1048_F143A5&plus_1_MXM-M
U2: MAX32664GWEA+T; 21-100241A_W161K1&plus_1_MXM
U3: PAM2401YPADJ; SON12_U-DFN3030-12_DIO-M
U4: PTPS7A2018PDBVR; DBV0005A-IPC_A
Y1: 32k768; Crystal_SMD_2012-2Pin_2.0x1.2mm

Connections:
+1V8: C2.1, C3.1, C5.1, R1.1, R2.1, R3.1, U1.11 (VDD), U2.A3 (VDD), U4.5 (OUT)
+3.3V: C7.1, J1.4, L1.1, R6.2, R7.2, U3.3 (EN), U3.4 (VIN), U4.1 (IN), U4.3 (EN)
+5V: C1.1, C6.1, R4.2, U1.9 (VLED+), U1.10 (VLED+), U3.9 (OUT), U3.10 (OUT)
GND: C1.2, C2.2, C3.2, C4.2, C5.2, C6.2, C7.2, J1.5, R5.2, U1.4 (PGND), U1.12 (GND), U2.B2 (VSS), U3.6 (AGND), U3.11 (PGND), U3.12 (PGND), U4.2 (GND)
HOST_SCL: J1.2, R7.1, U2.D1 (SLAVE_SCL)
HOST_SDA: J1.3, R6.1, U2.D2 (SLAVE_SDA)
HR_INT: R1.2, U1.13 (*INT), U2.C4 (HR_INT)
unnamed: L1.2, U3.1 (LX), U3.2 (LX)
unnamed: U2.A2 (32KIN), Y1.1
unnamed: U2.A1 (32KOUT), Y1.2
unnamed: C4.1, U2.A4 (VCORE)
unnamed: R4.1, R5.1, U3.7 (FB)
RST: J1.1, U2.B1 (RSTN)
SSR_SCL: R2.2, U1.2 (SCL), U2.B4 (SENSOR_SCL)
SSR_SDA: R3.2, U1.3 (SDA), U2.B3 (SENSOR_SDA)

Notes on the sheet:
I²C Pullup Resistors
MAX32664 Biometric HUB
LDO 3.3V to 1.8V
Connectors
DC-DC Converter
MAX30101 Pulse Oximeter and Heart Rate Sensor

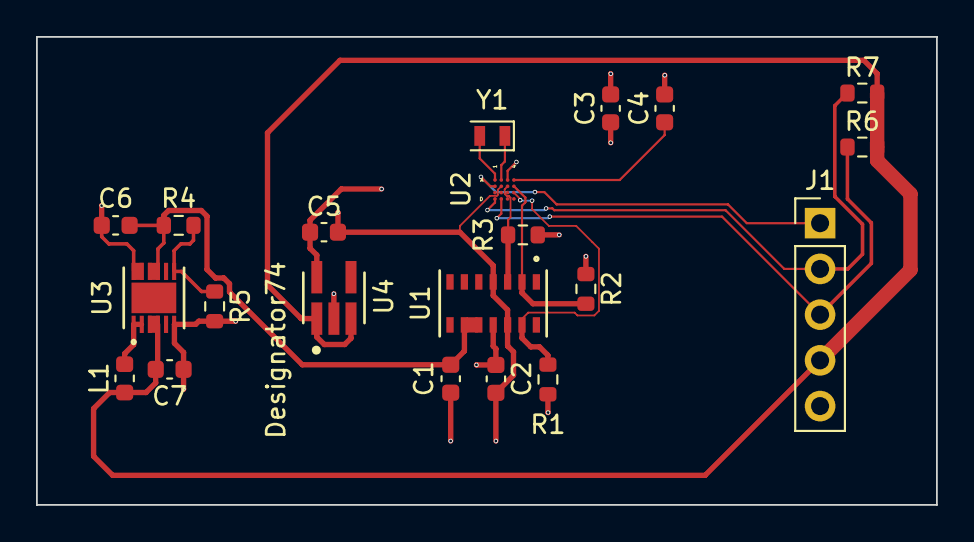
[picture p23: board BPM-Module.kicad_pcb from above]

Board: 2 copper layers, 50.0 x 26.0 mm, 21 parts (0 on the bottom side), 15 nets.

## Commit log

2025-04-27 Folder Architecture changes
    [Gringo.kicad_pcb, Gringo.kicad_sch]
2025-09-23 Ajout cahier des charges
2025-09-23 Rédaction cahier des charges V1
2025-09-28 Add components diagram
    Adding accelero + change health sensor
2025-12-10 BPM Module PCB
    * Schematics and PCB for the BPM module
    * BPM Module - DRC problems solving
    * BPM Module - Fabrication files
    [BPM-Module.kicad_pcb, BPM-Module.kicad_sch, bom.csv, designators.csv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]
2025-12-16 Comparison and final choices of main components
    * HR and IMU sensors sections
    * Sensors comparison
    * Updating the final choices table
    * Update for final component choices with IMU
    * Order request document partially filled
    * Theoric global consumption study
    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
    [Consumption-Gring-Go.xlsx]
2025-12-18 Custom Eval boards PCB
    * TableTestFootprints - 1.0
    Quelque pépins à régler en vue de faire des tests sur ce PCB.
    A voir avec Marius pour les pins utiles, haute fréquence, d'autres composants...
    * PCB test Marius - 3 composants faits
    Potentiellement rajouter certains composants avant de le commander (je vais laisser faire MARIUS)
    * Update the eval kit PCB with BPM module part
    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
    [Gringo.kicad_pcb, Gringo.kicad_sch, bom.csv, bpm-module.kicad_sch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]
2025-12-18 Update via diameter and hole diameter for evk PCB
    [Gringo.kicad_pcb]
2025-12-23 Fix the evk board with the adapted component packages (#36)
    * Correction before buy JLCPCB
    Remove of via down to 2 tiny component
    Change of clearance of the pads to pass routes
    To remove clearance : select all the pads > propriétés > Clearance Overrides and DON T PUT 0 (herited) but something like -0.001
    * Update scheme and PCB for evk boards with adapted component packages
    * Update zones
    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
    [Gringo.kicad_pcb, Gringo.kicad_sch, bom.csv, bpm-module.kicad_sch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]
2025-12-28 Update DOC/Cahier des charges.md
2026-01-20 Fix image URL in Cahier des charges.md
    Updated image source in the document and corrected the image URL for the project diagram.
2026-04-28 Add of Gringito Kicad project
    [Gringito.kicad_pcb, Gringito.kicad_sch]
2026-05-04 End schematics PCB Wireless Charge
    [Gringito.kicad_pcb, Gringito.kicad_sch, bom.csv, designators.csv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]
2026-05-06 V1 PCB Wireless charging
    [Gringito.kicad_pcb, recep.kicad_sch]
2026-05-06 V2 PCB / MODIFS DE PLAN / ERREURS
    [Gringito.kicad_pcb]
2026-05-11 final version + bom
    [BOMCOmplete.xlsx, Gringito.kicad_pcb, Gringito.kicad_sch, bom.csv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]
2026-05-11 corrections via pas au bon potentiel
    [Gringito.kicad_pcb]
